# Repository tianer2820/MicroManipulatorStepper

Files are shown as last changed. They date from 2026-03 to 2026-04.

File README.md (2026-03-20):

# Open Micro-Manipulator

This project contains an open source low-cost, easy-to-build motorized **XYZ Micro-Manipulator** motion control platform achieving submicron precision.
It's designed for applications such as optical alignment, probing electronic components, and microscopy.

Check out the YouTube video for more information about the device and how it is built:<br>
[An Open Source Motorized XYZ Micro-Manipulator - Affordable sub µm Motion Control](https://youtu.be/MgQbPdiuUTw)

<div style="display: flex; gap: 2%;">
  
  
</div>

Thanks to its parallel kinematic structure and miniature ball joints, it achieves good mechanical stiffness and a large range of motion.
The motors are off the shelf stepper motors driven by a 30 kHz closed loop controller and a very precise PWM signal.
A 'magnetic gearing' approach increases the resolution of the low-cost magnetic rotary encoders by a factor of 30 allowing for steps down to 50nm
(**Please mind the difference between resolution and accuracy**. The absolute accuracy is significantly worse.

The device can be controlled via simple G-Code commands over a USB serial interface and is thus easily integrated into other projects.
The firmware implements a complete motion planning stack with look-ahead for smooth and accurate path following capabilities.

## Getting Started

Below is a list of high level steps you can follow if you want to replicate the project. 
If you have questions or problems with the build or just want to discuss subjects related to the project, 
joint the projects community [Discord Server](https://discord.gg/maRvMVpa2Q).

1. Read this Document and watch the linked videos
2. Get the parts listed in [Bill of Materials](documentation/bom/bom.md)
3. Build the device and electronics
4. Change the hardware configuration according to your build [hw_config.h](firmware/MotionControllerRP/src/hw_config.h)
5. Upload firmware using VSCode with PlattformIO plugin
6. Calibrate axis

Also check out the setup guide for new devices: [Setup Guide](documentation/setup_guide/setup_guide.md)

## ✨NEW: Hardware Version 4.0
A new version of the hardware has been released, fixing several issues with the previous design:

- Self collision during homing fixed.
- Connection of ball joint block with screws only was not well constrained and could rotated a bit.
- No reliable way to ensure consistent linkage rod length
- Unnecessary ball joint friction
- Accurate ball position heavily dependet on print quality and corner rounding
- Rubber bands could not be changed or removed once glued in.

A video about the improved ball joint and linkage manufactoring process can be found on YouTube: [Better Ball Joints for the Open Micro-Manipulator](https://www.youtube.com/watch?v=NM2KXvRGmpg)
Also the FreeCAD model was restructured and improved and now includes all pins and fasteners. It now provides a reference for all required mechanical parts. 

<div style="display: flex;">
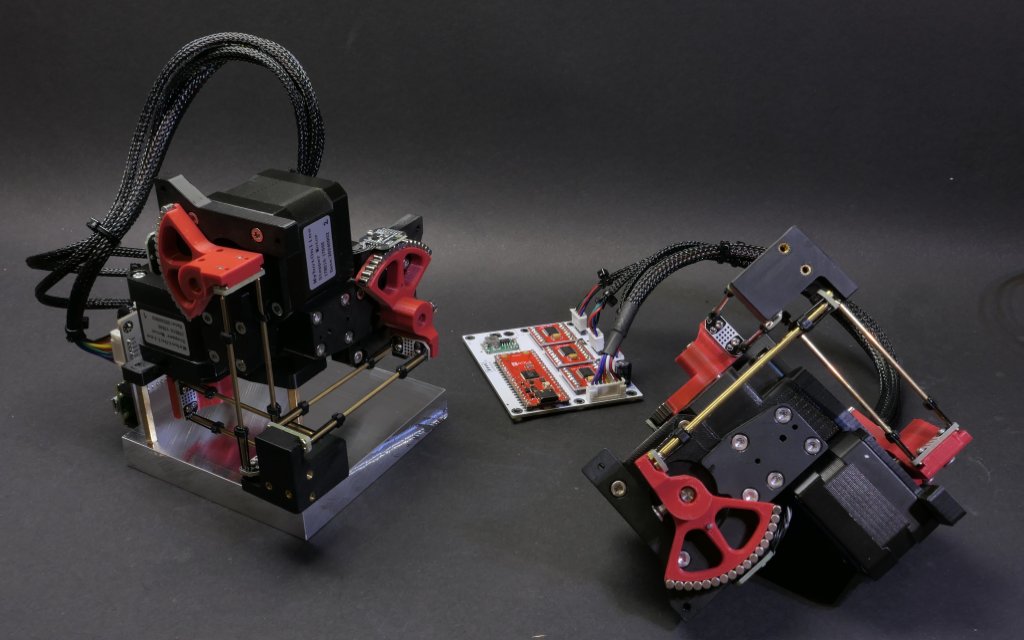
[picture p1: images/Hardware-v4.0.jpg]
Open Micro-Manipulator GUI
    
</div>

WARNING: BOM is not updated yet...

## Open Micro-Manipulator GUI
To make testing and using the Open-Micro Manipulator easy and convenient a python control program with a graphical user interface is provided here: [Open Micro-Manipulator GUI](https://github.com/0x23/OpenMicroManipulatorGUI).
It has simple controlls to move the device around, while also displaying a live camera feed (e.g. from a microscope camera). Additional features, include a simple g-code runner and realtime mouse control (e.g. for Biology applications).

<div style="display: flex;">
    Open Micro-Manipulator GUI
</div>

## 🐍 Python-API

The lightweight Python API handles all serial communication and provides convenient command execution and debug message printing.
The interface includes functions to home, move, and calibrate the device, as well as to query device information.

This library has not been published to pypi yet but it can be installed by running the following pip command. This can also be added to your projects requirements.txt:

```bash
pip3 install "git+https://github.com/0x23/MicroManipulatorStepper/#subdirectory=software/PythonAPI"
```

If you would like to use the calibration plotter then you will need the additional `plotter` optional dependency.

## Usage Example
```python
from open_micro_stage_api import OpenMicroStageInterface

# create interface and connect
oms = OpenMicroStageInterface(show_communication=True, show_log_messages=True)
oms.connect('/dev/ttyACM0')

# run this once to calibrate joints
# for i in range(3): oms.calibrate_joint(i, save_result=True)

# home device
oms.home()

# move to several x,y,z positions [mm]
oms.move_to(0.0, 0.0, 0.0, f=10)
oms.move_to(3.1, 4.1, 5.9, f=26)
oms.move_to(0.0001, 0.0, 0.0, f=10)

# wait for moves to finish
oms.wait_for_stop()
```

## API Functions (most relevant functions only)
```python
connect(port, baud_rate=921600)
disconnect()
set_workspace_transform(transform)
get_workspace_transform()
home(axis_list=None)
calibrate_joint(joint_index, save_result)
move_to(x, y, z, f, move_immediately, blocking, timeout)
set_tool_output(tool_idx, output_value, immediate)
set_pose(x, y, z)
dwell(time_s, blocking, timeout)
enable_motors(enable)
wait_for_stop(polling_interval_ms, disable_callbacks)
set_max_acceleration(linear_accel, angular_accel)
set_servo_parameter(pos_kp, pos_ki, vel_kp, vel_ki, vel_filter_tc)
```
## ✨ Firmware v1.0.4

Firmware 1.0.4 comes with many smaller improvements and bugfixes and a great new feature as well:

 - **Tools**: Tool usage (for example for laser engraving) is now supported on the two GPIO pins of J5 on the pcb.
              Tools are integrated into the planner and run fast and with correct timing when executing g-code.
              The tools support PWM (using the PIO feature to squeeze out extra channels without relying on software PWM).

   Example usage:
   ```
     M3 T0 S0.7  // set pwm output of tool 0 to 70%
     G4 S0.001   // dwell command (or any other motion command) - necessary to apply the tools output
   ```
   
- **Calibration**: Calibration has now some addition error checks to improve error reporting of potential problems like encoder alignment.
- **Kinematic Model Parameter**: Initialization code has been cleaned up and better comments where added to the parameters. Parameters are preset for HW v4.0 but you can toggle back to the old HW-v3.0 parameters if necessary.
- **Bugfixes**: smaller bugfixes

IMPORTANT: If you have **Hardware Version v3.0** you need to switch back to the old kinematic parameters in the [kinematic_model_delta3d.cpp](firmware/MotionControllerRP/src/kinematic_models/kinematic_model_delta3d.cpp) file (there is an #define for that at the top).

## Firmware v1.0.1

This update improves calibration, homing, logging, and adds several new G-Code commands.

### Improvements
- **Homing**: parallel homing support, higher repeatability, more accurate geometric reference  
- **Joint calibration**: refined procedure, persistent flash storage (no recalibration after reboot)  
- **Logging**: clearer and more detailed output  

### New G-Code Commands
- `G28` — Home joints (supports homing multiple axis simultanously for faster startup)
- `G24` — Set pose command (directly sets servo targets, bypassing motion controller)  
- `M17/M18` — Enable/Disable motors (with pose recovery from encoders on enable)  
- `M51` — Read encoder values  
- `M55` — Set servo loop parameters 
- `M56` — Joint calibration (with save-to-flash option)  
- `M57` — Read various information about the device state  
- `M58` — Read firmware version

## ⚙ CAD-Files

All CAD models are made in **FreeCAD** to allow everyone to view and modify the design without subscribing or paying for a proprietary CAD solution.
Note that most components are already designed with the goal to make them easily machinable on a 3-Axis CNC-Mill.
You can also 3D-Print the parts but have to live with thermal drift (carbon filled filaments can reduce this problem).

<div style="display: flex;">
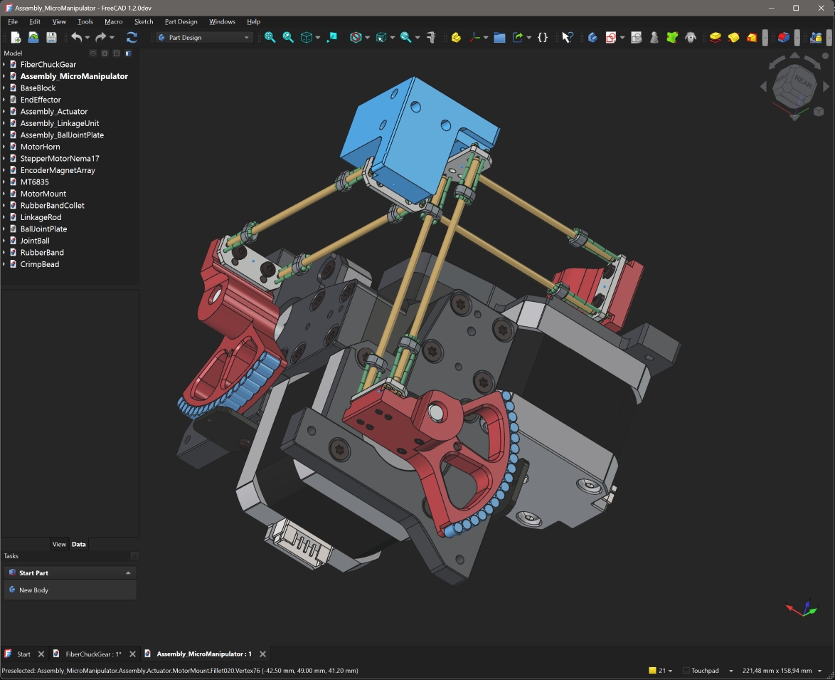
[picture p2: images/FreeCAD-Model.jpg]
FreeCAD Model
    
</div>

<br>

The CAD files can be found here: [CAD Models](construction).
Please note that FreeCAD version **1.2.0dev** was used, and the files might not work with older versions.

STL files for printing can be found here: [STL Files](construction/STL_3D_Printing/)

## ⚙ Kinematic Model

The kinematic model is defined here: [kinematic_model_delta3d.cpp](firmware/MotionControllerRP/src/kinemtaic_models/kinematic_model_delta3d.cpp).
Please check the dimensions of your build against the values set in the constructor. In particular, make sure the arm length matches.

## ⚙ Electronics

IMPORTANT: If you fabricated PCB version v1.2 (see version label on the board) you need to drill out a misplaced via on diode D1 that shorts 5V rail to ground (See [repair image](electronics/pcb_v1.2_fix.jpg) ). The problem was fixed in v1.3.

The electronics are designed in **KiCAD** and only commonly available modules (motor drivers and MCU boards) are used and connected by a simple PCB. No SMD soldering is required to populate the board to make the build extra accessible.
For usual winding resistance of your motors, the device should be powered by $${\color{lightgreen} 5V-6V }$$ (2A) to keep current and heating to a reasonable level.

<div style="display: flex; gap: 5%;">
  
  
</div>

The repository now also contains the fabrication files that can be directly uploaded to the PCB manufacturer.

## ⚙ Firmware

The firmware is written in C++ and takes some inspiration from the 'SimpleFOC' project. It aims to be streamlined and readable without any extra fuss, focusing on the hardware used in this project.
It implements path planning with look-ahead and, unlike many other motion controller projects, supports true 6DOF-Pose interpolation and planning, making it ready for driving hexapod motion platforms; that may or may not be the next step for this project.

You may find configuration for pin numbers, motor type, and other parameters in [hw_config.h](firmware/MotionControllerRP/src/hw_config.h). Please check them before uploading the firmware.

<div style="display: flex; gap: 2%;">
  
  
</div>

### Building and Flashing the Firmware

For building and flashing the firmware, Visual Studio Code (available for free on Windows and Linux) is recommended.
Install the PlatformIO add-on and open the firmware folder. You can now build and flash the firmware like any other PlatformIO project.

## ⚙ G-Code Interface

The firmware supports only a small subset of G-Code commands listed below.  
Each command is acknowledged with either an **`ok`** or **`error`** response.  

If a command provides additional information (e.g., the *get position* command), that information is returned **before** the `ok` message.  
The client must wait for an acknowledgment from the previous command before sending the next one—otherwise, behavior is undefined.
| Command           | Description                                                                 |
|-------------------|-----------------------------------------------------------------------------|
| `G0 X Y Z F`   | Move the end-effector in a straight line to the specified position. <br>• `X`, `Y`, `Z`: target positions <br>• `F`: feed rate |
| `G1 X Y Z F`   | Same as `G0`.                                                              |
| `G4 S/P`       | Dwell/pause for a specified time. <br>• `S`: seconds <br>• `P`: milliseconds |
| `G24 X Y Z A B C` | Directly set current pose for servo loops with optional rotation vector* `A`, `B`, `C`. |
| `G28 A-F`      | Home one or more joints. <br>• Optional joint selection `A`–`F`.           |
| `M3`           | Set Tool output. <br>• `T`: tool index <br>• `S`: output value (0.0..1.0) <br> Note: new values is only applied on the next motion or dwell command         |
| `M17`          | Enable motors and read current pose as the start pose.                     |
| `M18`          | Disable motors.                                                            |
| `M50`          | Get current internal pose. (Encoders are not read here)                                   |
| `M51`          | Get current encoder angles (in degrees) and raw encoder values.              |
| `M52`          | Get the number of items in the planner queue.                               |
| `M53`          | Check if all planned moves are finished (`1` = finished, `0` = not finished). |
| `M55 A B C D F` | Set servo loop parameters. <br>• `A`, `B`: position PI controller gains (P and I) <br>• `C`, `D`: velocity PI controller gains (P and I) <br>• `F`: velocity filter time constant |
| `M56 J S`      | Calibrate a joint. <br>• `J`: joint index <br>• `S`: save calibration result |
| `M57`          | Get device and servo loop info: homing/calibration state, angles, loop frequencies, and file list. |
| `M58`          | Get firmware version.                                                      |
| `M204 L A`     | Set linear and angular acceleration. <br>• `L`: linear acceleration <br>• `A`: angular acceleration |

*Note: The communication protocol uses 3D vectors for rotations. The direction represents the rotation axis and the length of the vector represents the angle of rotation around the axis.

## ❤️ Support

If you'd like to support this project, consider the following:

- **Contribute to the build guide** – Help improve or expand the build instructions by submitting pull requests or opening issues with suggestions.
- **Characterize typical radial stepper motor shaft error motion** – Measure radial error motion of the shaft of multiple Nema-17 stepper motors (see Cylos Garage for more information about the subject: https://www.youtube.com/watch?v=gt2gK-oxy5s).
- **Give feedback on the build experience** – Let us know what worked, what didn’t, and how the process could be smoother for others.
- **Support the project on Ko-fi** – If you find this project valuable, you can support it financially via [Ko-fi](https://ko-fi.com/diffractionlimited) ☕.

## Youtube Video
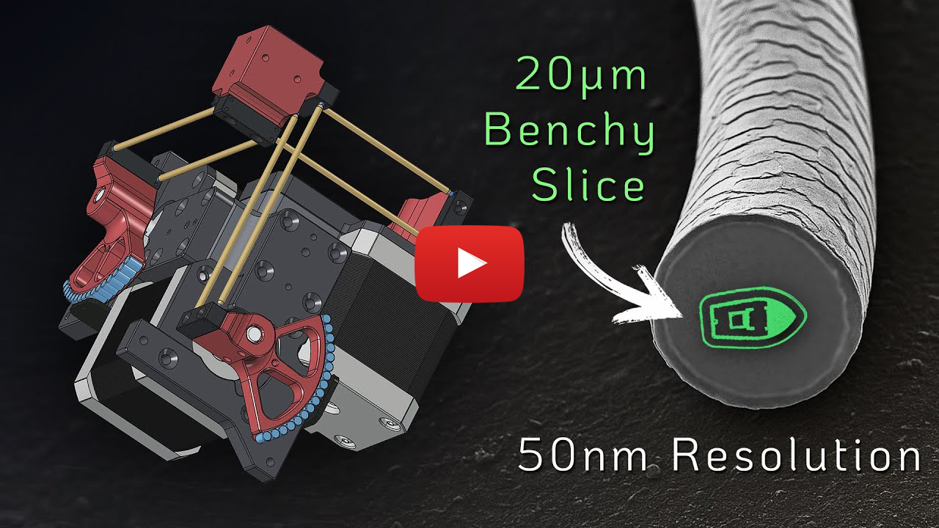
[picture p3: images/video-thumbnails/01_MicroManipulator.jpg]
Watch the video (https://youtu.be/MgQbPdiuUTw)

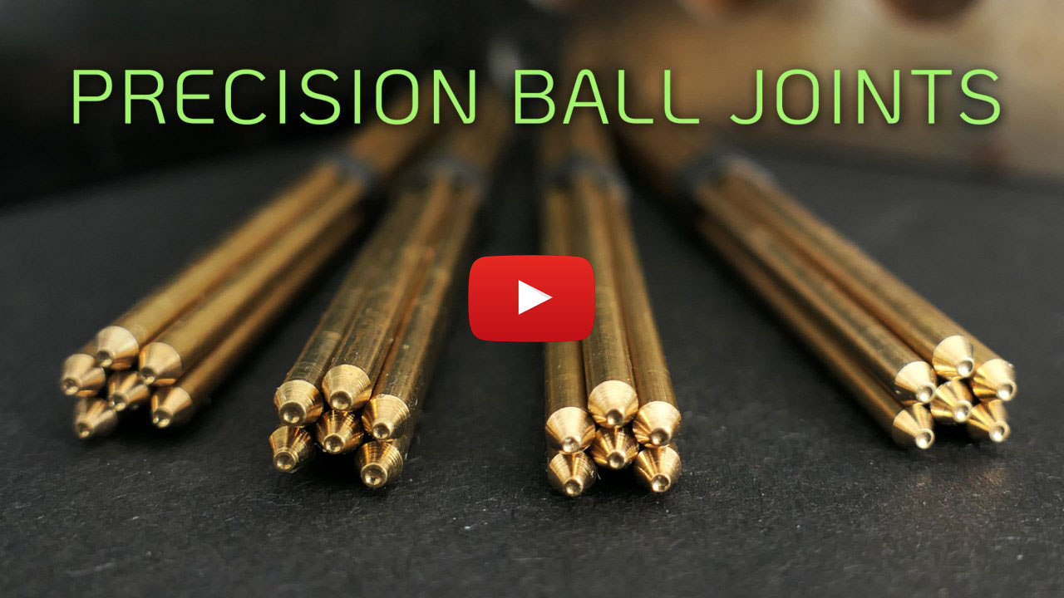
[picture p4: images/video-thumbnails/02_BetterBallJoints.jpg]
Better Ball Joints for the Open Micro-Manipulator (https://youtu.be/MgQbPdiuUTw)


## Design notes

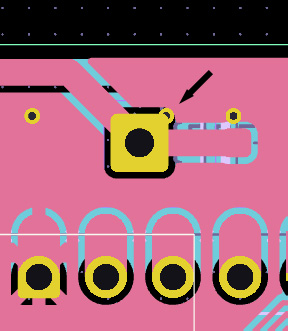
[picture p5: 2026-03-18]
electronics/control_board/pcb_v1.2_fix.jpg

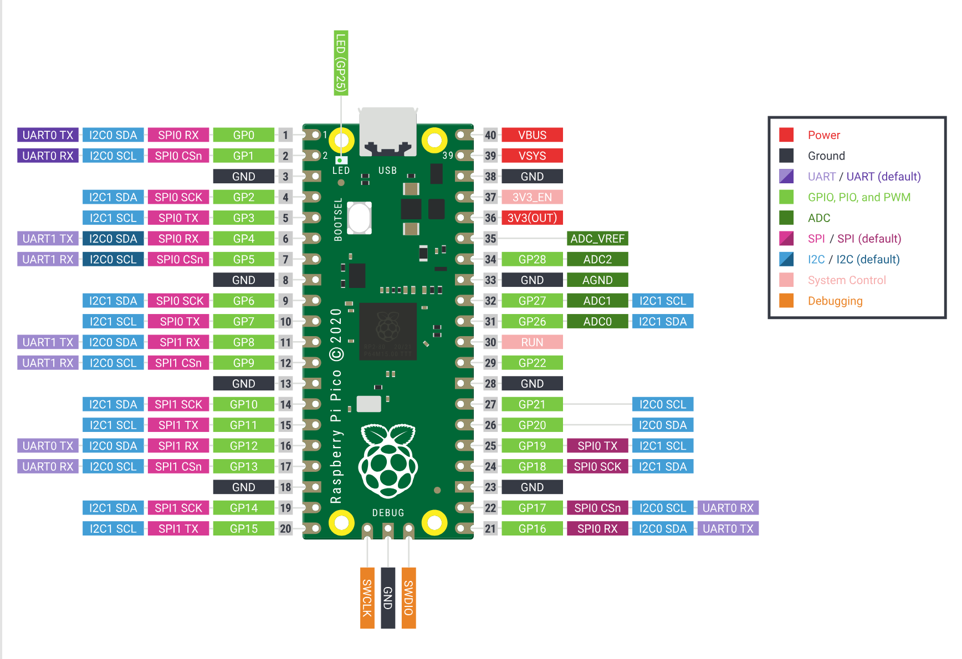
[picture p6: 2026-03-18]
firmware/MotionControllerRP/Rp2350-Pico_Pinout.png

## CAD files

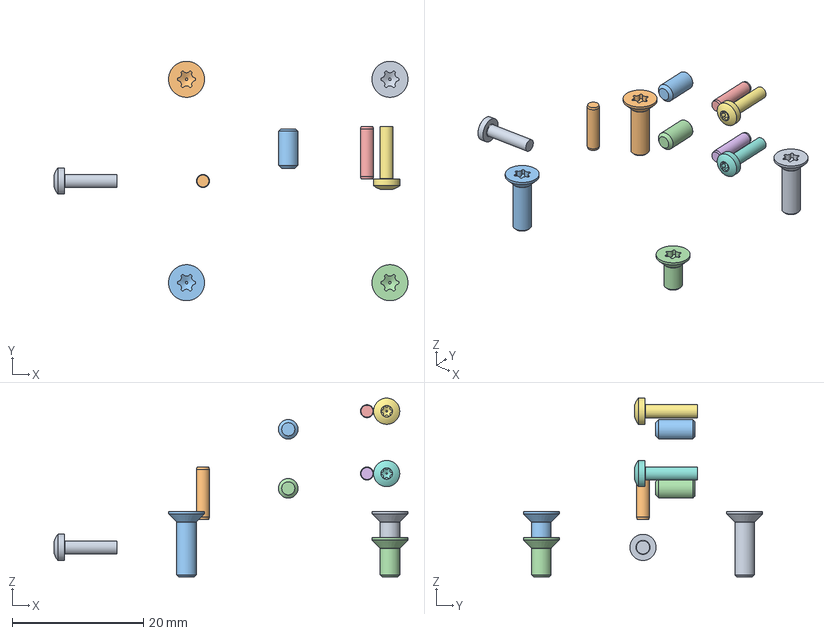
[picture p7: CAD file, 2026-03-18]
construction/micro_manipulator/Assembly_Actuator.FCStd
53.9 x 36.5 x 27.2 mm
M3x10-Screw x 2
M3x10-Screw008 x 2
M3x10-Screw009 x 2
M3x6-Screw x 2
2 mmx8-Pin x 2
2 mmx8-Pin012 x 2
M2x8-Screw x 2
M2x8-Screw009 x 2
M2x8-Screw004 x 2
2 mmx8-Pin011 x 2
M3x6-Screw003 x 2
M3x6-Screw004 x 2

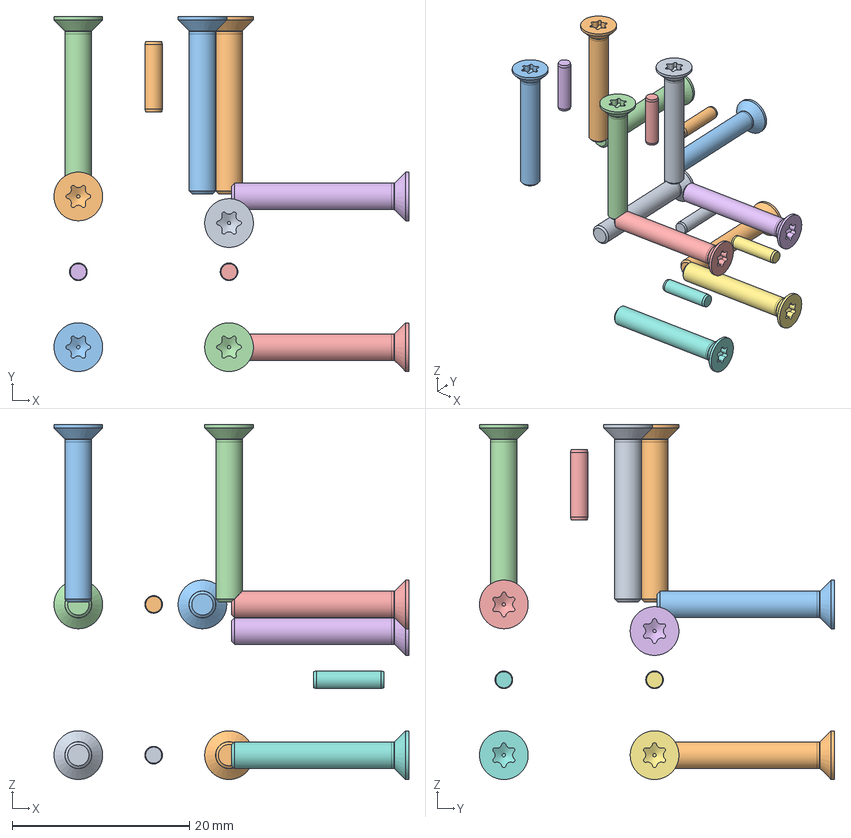
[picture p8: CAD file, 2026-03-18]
construction/micro_manipulator/Assembly_MicroManipulator.FCStd
40.0 x 40.0 x 40.0 mm
M3x20-Screw x 2
M3x20-Screw281 x 2
M3x20-Screw282 x 2
M3x20-Screw283 x 2
M3x20-Screw277 x 2
M3x20-Screw278 x 2
M3x20-Screw279 x 2
M3x20-Screw280 x 2
M3x20-Screw262 x 2
M3x20-Screw263 x 2
M3x20-Screw264 x 2
M3x20-Screw265 x 2
2 mmx8-Pin027 x 2
2 mmx8-Pin028 x 2
2 mmx8-Pin029 x 2
2 mmx8-Pin030 x 2
2 mmx8-Pin031 x 2
2 mmx8-Pin032 x 2

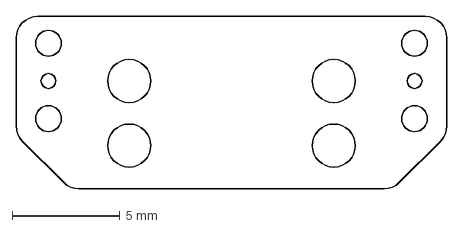
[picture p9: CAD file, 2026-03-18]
construction/micro_manipulator/balljoint_plate_pcb/BallJointPlate-Contour.dxf
20.0 x 8.00 mm

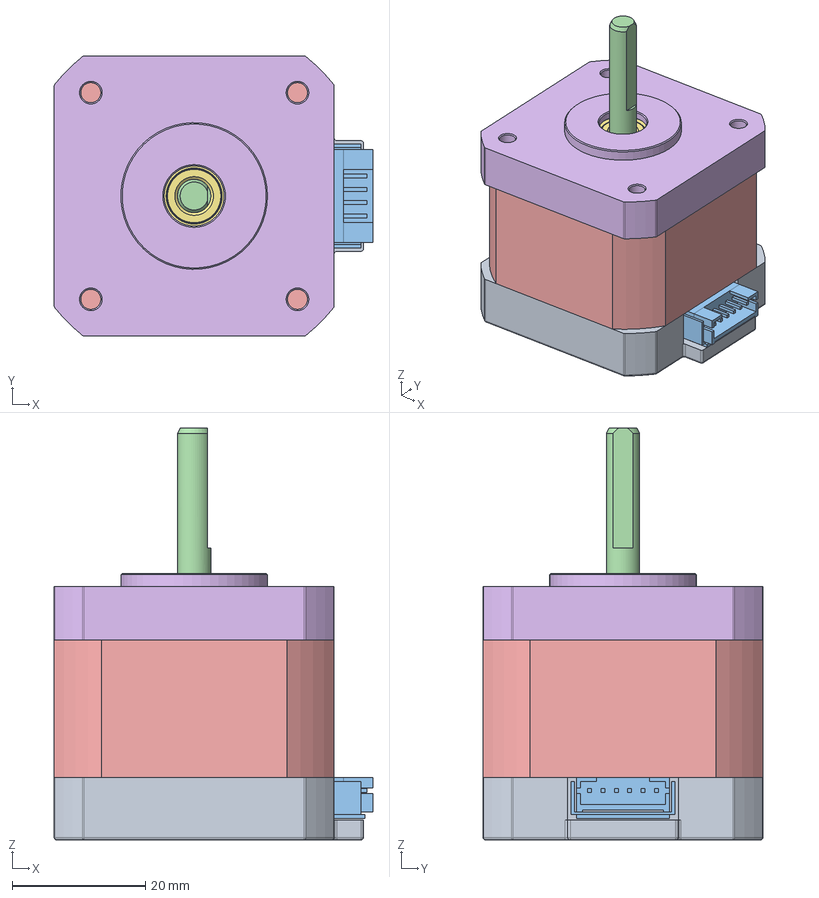
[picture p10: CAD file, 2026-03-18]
construction/micro_manipulator/StepperMotorNema17.FCStd
47.8 x 42.0 x 61.8 mm
rear end cap
rear bearing
connector
shaft
stator
front end cap
front bearing
M3x10-Screw
M3x10-Screw004
M3x10-Screw005
M3x10-Screw006

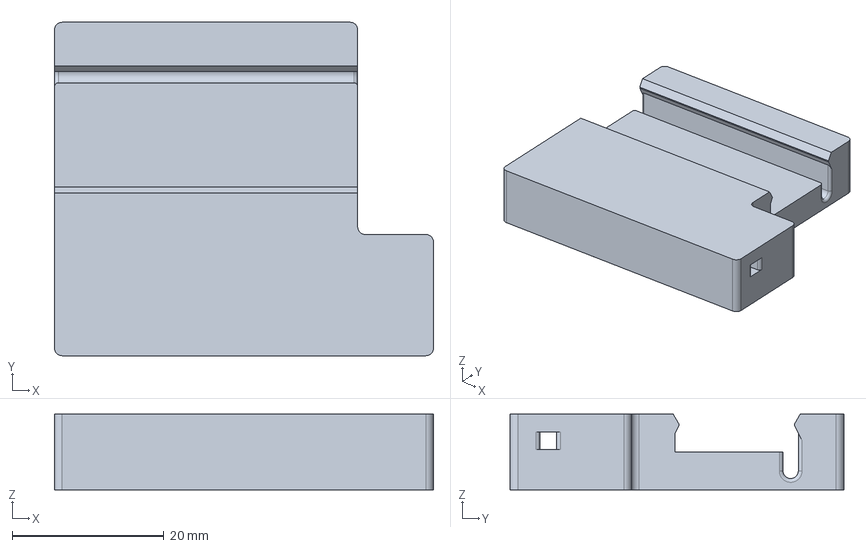
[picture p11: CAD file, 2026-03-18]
construction/tools/rod_embossing_tools/rod_lenth_setting_press/rod_guide.FCStd
50.0 x 44.0 x 10.0 mm

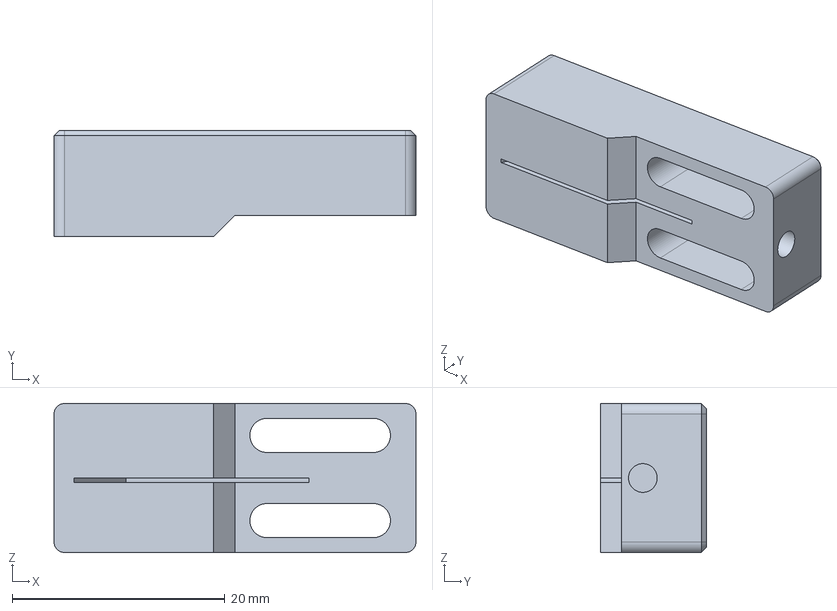
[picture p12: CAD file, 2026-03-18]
construction/tools/rod_embossing_tools/rod_sharper/BladeCarrier.FCStd
34.0 x 10.0 x 14.0 mm

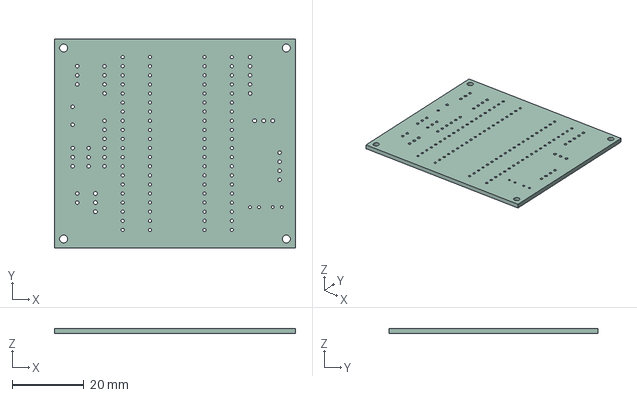
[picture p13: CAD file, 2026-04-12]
electronics/rot_platform_pcb/rot_platform_pcb.step
67.3 x 58.4 x 1.51 mm

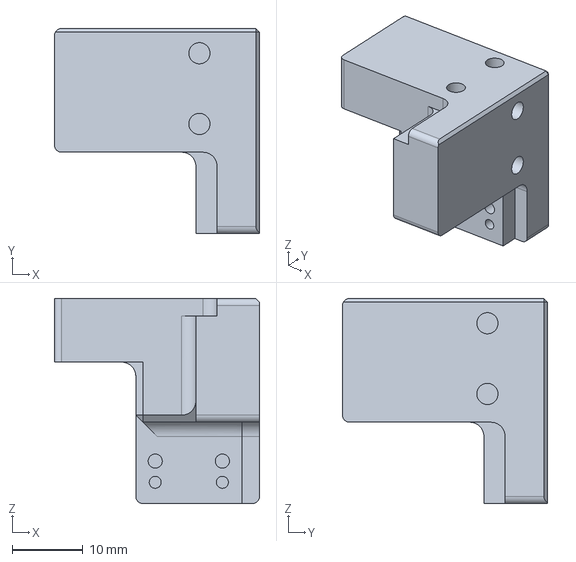
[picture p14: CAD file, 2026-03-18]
construction/micro_manipulator/EndEffector.FCStd
29.0 x 29.0 x 29.0 mm

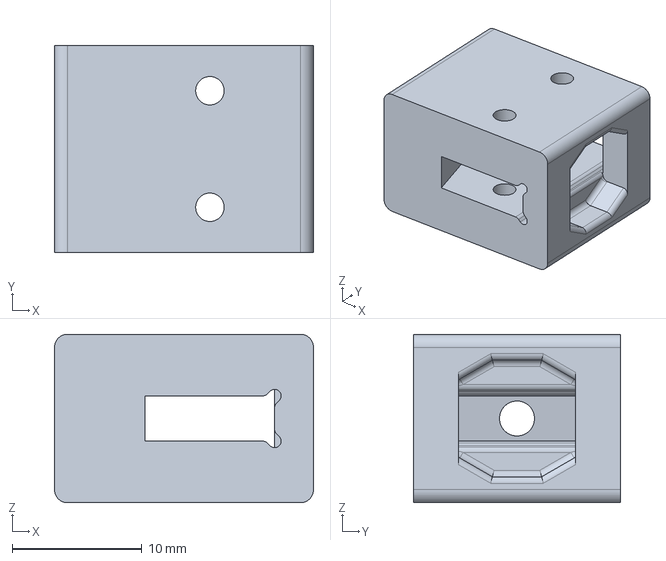
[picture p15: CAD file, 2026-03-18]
construction/tools/rod_embossing_tools/rod_lenth_setting_press/caliper_clamp.FCStd
20.0 x 16.0 x 13.0 mm

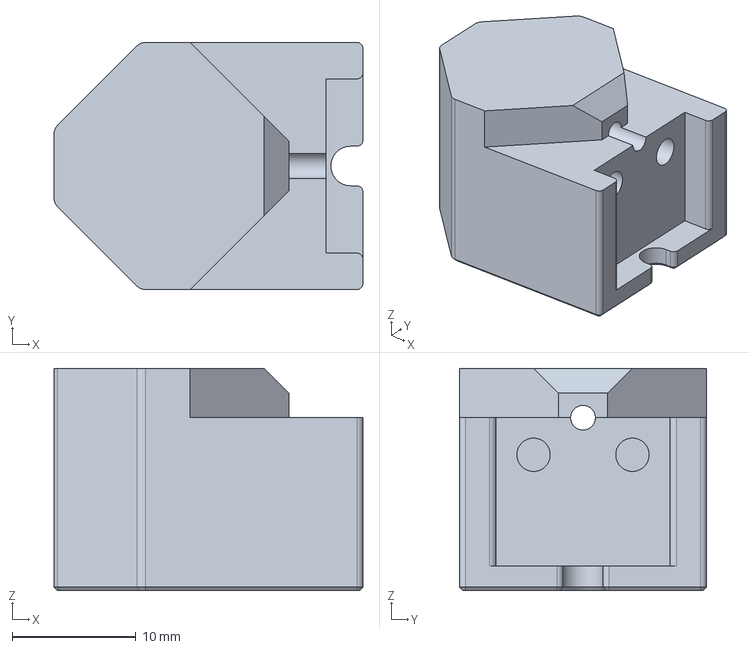
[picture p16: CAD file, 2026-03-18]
construction/tools/rod_embossing_tools/rod_sharper/RodGuide.FCStd
25.0 x 20.0 x 18.0 mm

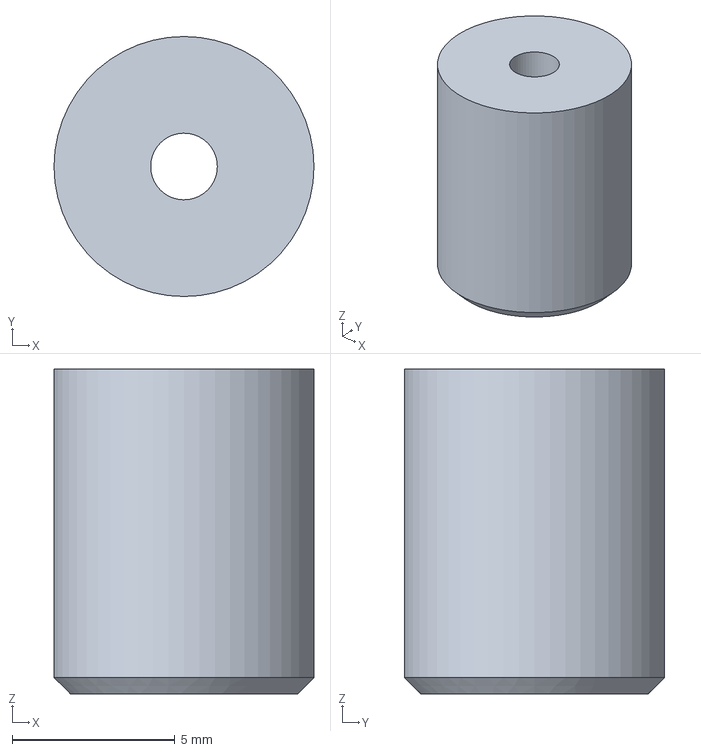
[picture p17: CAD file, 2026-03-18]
construction/tools/rod_embossing_tools/rod_lenth_setting_press/rod_collet.FCStd
8.00 x 8.00 x 10.0 mm

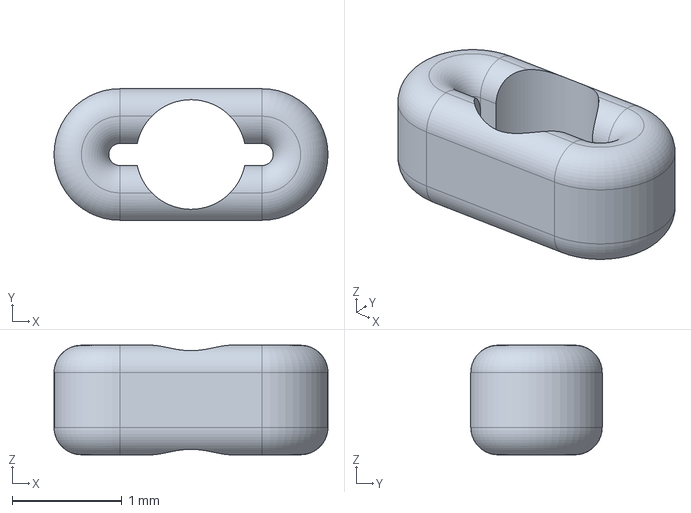
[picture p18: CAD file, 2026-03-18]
construction/micro_manipulator/CrimpBead.FCStd
2.50 x 1.20 x 1.00 mm

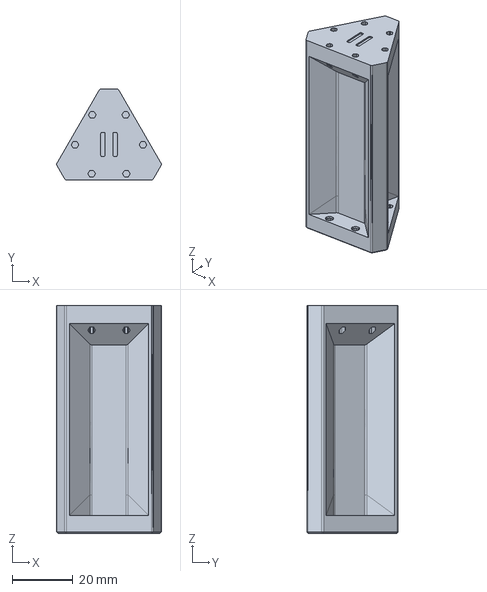
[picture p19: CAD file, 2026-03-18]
construction/tools/rod_embossing_tools/rod_lenth_setting_press/RodGrindingJig_B.FCStd
34.5 x 30.1 x 75.0 mm

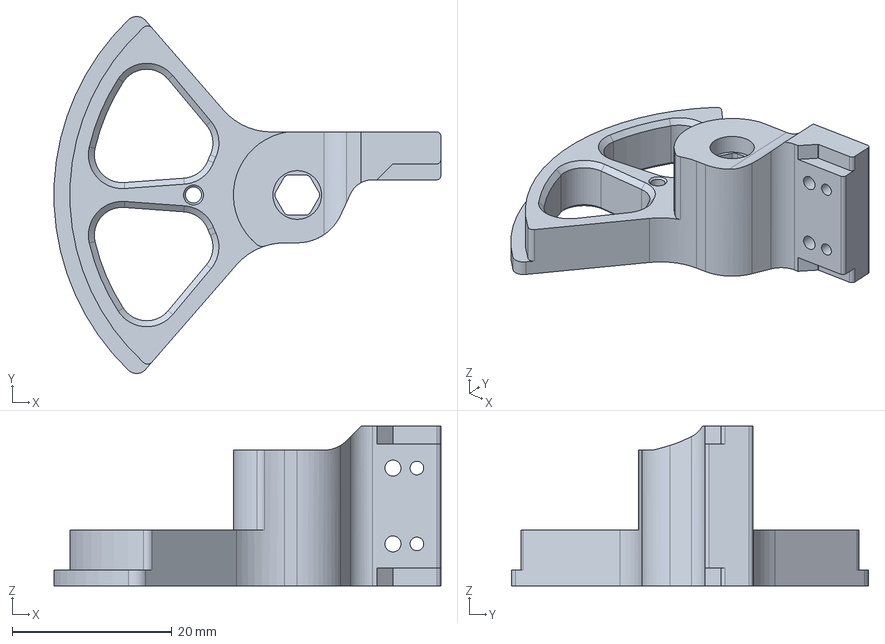
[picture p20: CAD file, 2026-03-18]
construction/micro_manipulator/MotorHorn.FCStd
48.5 x 44.7 x 20.0 mm

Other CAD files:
construction/micro_manipulator/Assembly_EndEffector.FCStd
construction/micro_manipulator/Assembly_BallJointPlate.FCStd
construction/micro_manipulator/Assembly_LinkageUnit.FCStd
construction/tools/rod_embossing_tools/rod_lenth_setting_press/RodGrindingJig_A.FCStd
construction/micro_manipulator/BallJointPlate.FCStd
construction/micro_manipulator/BaseBlock.FCStd
construction/micro_manipulator/EncoderMagnet.FCStd
construction/micro_manipulator/EncoderMagnetArray.FCStd
construction/micro_manipulator/JointBall.FCStd
construction/micro_manipulator/LinkageRod.FCStd
construction/micro_manipulator/MT6835.FCStd
construction/micro_manipulator/MotorMount.FCStd
construction/micro_manipulator/RubberBand.FCStd
construction/micro_manipulator/RubberBandCollet.FCStd

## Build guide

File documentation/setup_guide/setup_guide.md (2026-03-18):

# Setup Guide

This guide walks you through the setup of your new **Open Micro-Manipulator** device.

## Checklist for New Devices

1. **Was the mechanical limit pin added to the rotor?**  
   This pin is required for proper homing of the device.

    <div style="display: flex;">
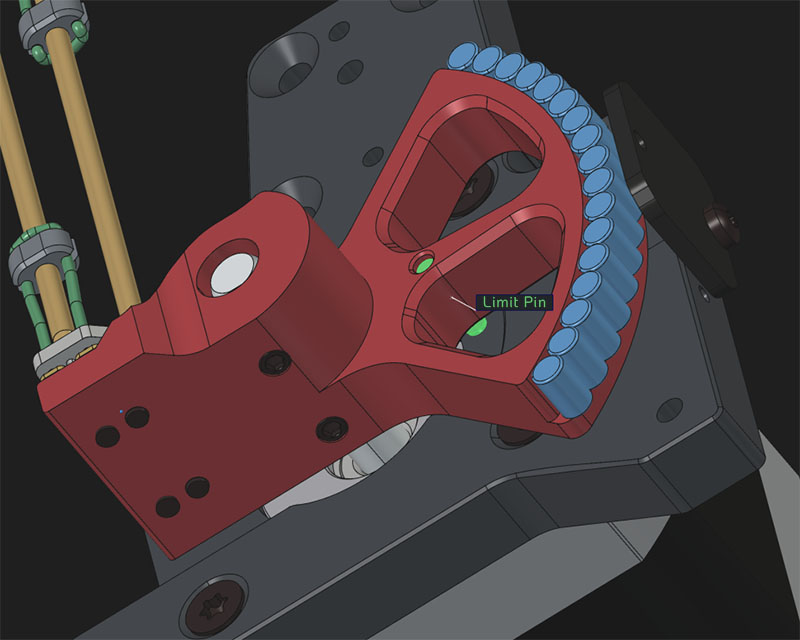
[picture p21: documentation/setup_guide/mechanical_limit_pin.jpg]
Mechanical Limit Pin
        
    </div>

2. **Are the screws that secure the rotor to the motor shaft installed?**  
   If the rotor is not firmly attached, it may slip imperceptibly during homing or other movements, leading to problems during calibration and homing.

3. **Is the homing direction correct?**  
   During the homing command (`G28`), the end effector should move toward the base.  
   If it moves in the opposite direction, rewire the motor to reverse its direction.

## Calibration and Checking the Encoders

You can use the calibration plotter to check if your encoders are working as expected.
On the left you see a good calibration on the right a bad calibration.

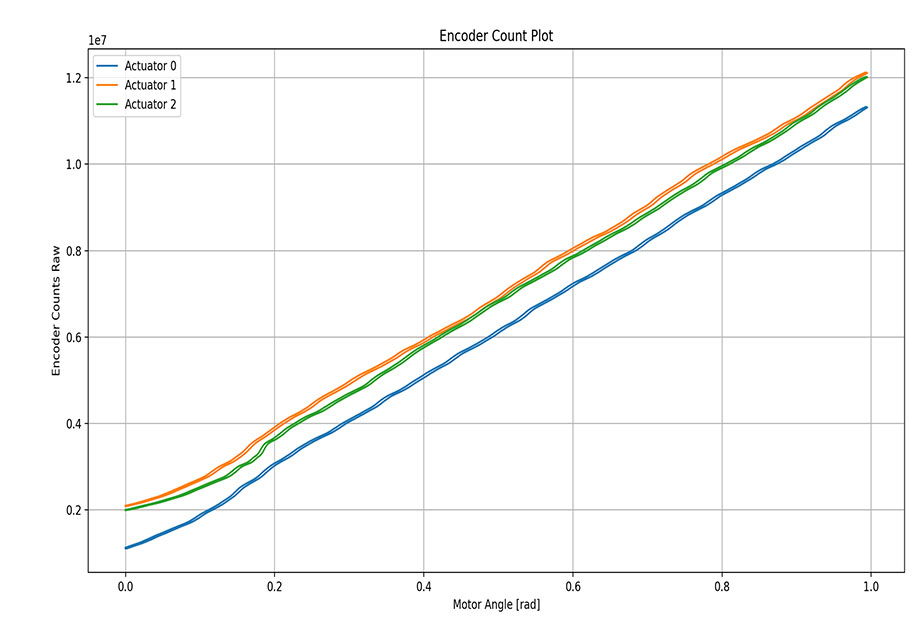
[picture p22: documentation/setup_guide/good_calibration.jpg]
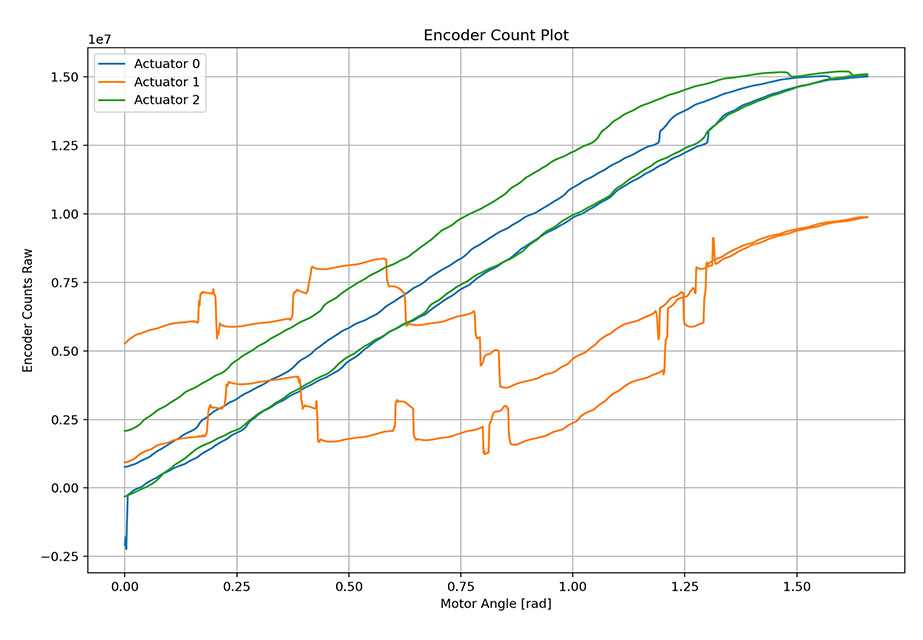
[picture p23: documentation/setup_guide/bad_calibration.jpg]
|  |  |
:--:|:--:
| **Good calibration** | **Bad calibration** |

THIS DOCUMENT IS UNFINISHED AND WORK IN PROGRESS...

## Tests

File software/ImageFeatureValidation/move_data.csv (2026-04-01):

From Position | To Position | Expected (um) | Actual (um) | Difference (um) | Feed
(-7.000000000,0.000000000) | (0.001000000,0.000000000) | 1 | 2.947063171 | 1.947063171 | 50
(0.001000000,0.000000000) | (0.002000000,0.000000000) | 1 | 1.324202497 | 0.324202497 | 50
(0.002000000,0.000000000) | (0.001000000,0.000000000) | 1 | 0.947177088 | -0.052822912 | 50
(0.001000000,0.000000000) | (0.000000000,0.000000000) | 1 | 1.716676845 | 0.716676845 | 50
(0.000000000,0.000000000) | (0.000000000,0.001000000) | 1 | 2.948005388 | 1.948005388 | 50
(0.000000000,0.001000000) | (0.000000000,0.002000000) | 1 | 2.185358535 | 1.185358535 | 50
(0.000000000,0.002000000) | (0.000000000,0.001000000) | 1 | 1.970507707 | 0.970507707 | 50
(0.000000000,0.001000000) | (0.000000000,0.000000000) | 1 | 2.121842258 | 1.121842258 | 50
(0.000000000,0.000000000) | (0.000707000,0.000707000) | 0.999848989 | 2.444252178 | 1.444403189 | 50
(0.000707000,0.000707000) | (0.001414000,0.001414000) | 0.999848989 | 2.787920685 | 1.788071696 | 50
(0.001414000,0.001414000) | (0.000707000,0.000707000) | 0.999848989 | 2.839523164 | 1.839674176 | 50
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

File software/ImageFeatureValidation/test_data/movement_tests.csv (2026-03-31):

x | y | feed | delay
0.001000 | 0.000000 | 50.0
0.002000 | 0.000000 | 50.0
0.001000 | 0.000000 | 50.0
0.000000 | 0.000000 | 50.0
0.000000 | 0.001000 | 50.0
0.000000 | 0.002000 | 50.0
0.000000 | 0.001000 | 50.0
0.000000 | 0.000000 | 50.0
0.000707 | 0.000707 | 50.0
0.001414 | 0.001414 | 50.0
0.000707 | 0.000707 | 50.0
0.000000 | 0.000000 | 50.0
-0.000707 | 0.000707 | 50.0
0.000000 | 0.001414 | 50.0
0.000707 | 0.000707 | 50.0
0.000000 | 0.000000 | 50.0
0.001000 | 0.000000 | 50.0
0.000293 | 0.000707 | 50.0
0.001000 | 0.001414 | 50.0
0.001707 | 0.000707 | 50.0
0.001000 | 0.000000 | 50.0
0.000000 | 0.000000 | 50.0
-0.000707 | -0.000707 | 50.0
0.000293 | -0.000707 | 50.0
0.001293 | -0.000707 | 50.0
0.000586 | 0.000000 | 50.0
0.000000 | 0.000000 | 50.0
0.001000 | 0.000000 | 50.0
0.002000 | 0.000000 | 50.0
0.001000 | 0.000000 | 50.0
0.000000 | 0.000000 | 50.0
0.000000 | 0.001000 | 50.0
0.000000 | 0.002000 | 50.0
0.000000 | 0.001000 | 50.0
0.000000 | 0.000000 | 50.0
0.000707 | 0.000707 | 50.0
0.001414 | 0.001414 | 50.0
0.000707 | 0.000707 | 50.0
0.000000 | 0.000000 | 50.0
-0.000707 | 0.000707 | 50.0
0.000000 | 0.001414 | 50.0
0.000707 | 0.000707 | 50.0
0.000000 | 0.000000 | 50.0
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

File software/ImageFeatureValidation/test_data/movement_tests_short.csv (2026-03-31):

x | y | feed | delay
0.01000 | 0.00000 | 50.0
0.02000 | 0.00000 | 50.0
0.01000 | 0.00000 | 50.0
0.00000 | 0.00000 | 50.0
0.00000 | 0.01000 | 50.0
0.00000 | 0.02000 | 50.0
0.00000 | 0.01000 | 50.0
0.00000 | 0.00000 | 50.0
0.00707 | 0.00707 | 50.0
0.01414 | 0.01414 | 50.0
0.00707 | 0.00707 | 50.0
0.00000 | 0.00000 | 50.0
-0.00707 | 0.00707 | 50.0
0.00000 | 0.01414 | 50.0
0.00707 | 0.00707 | 50.0
0.00000 | 0.00000 | 50.0
0.01000 | 0.00000 | 50.0
0.00293 | 0.00707 | 50.0
0.01000 | 0.01414 | 50.0
0.01707 | 0.00707 | 50.0
0.01000 | 0.00000 | 50.0
0.00000 | 0.00000 | 50.0
-0.00707 | -0.00707 | 50.0
0.00293 | -0.00707 | 50.0
0.01293 | -0.00707 | 50.0
0.00586 | 0.00000 | 50.0
0.00000 | 0.00000 | 50.0

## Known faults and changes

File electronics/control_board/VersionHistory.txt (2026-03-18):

*** v1.3 ****************************

 - Fixed critical problem with PCB layout, where 5V rail was shorted to GND on one of the diode pins of D1.
 
*** v1.2 ****************************

- added diode on 5V mcu supply to prevent motors from being powered backwards through the stepdown converter.

*** v1.1 ****************************

- Silkscreen on encoder connector was wrong: labels for CS1 and CS3 where swapped

*** v1.0 ****************************

Initial version

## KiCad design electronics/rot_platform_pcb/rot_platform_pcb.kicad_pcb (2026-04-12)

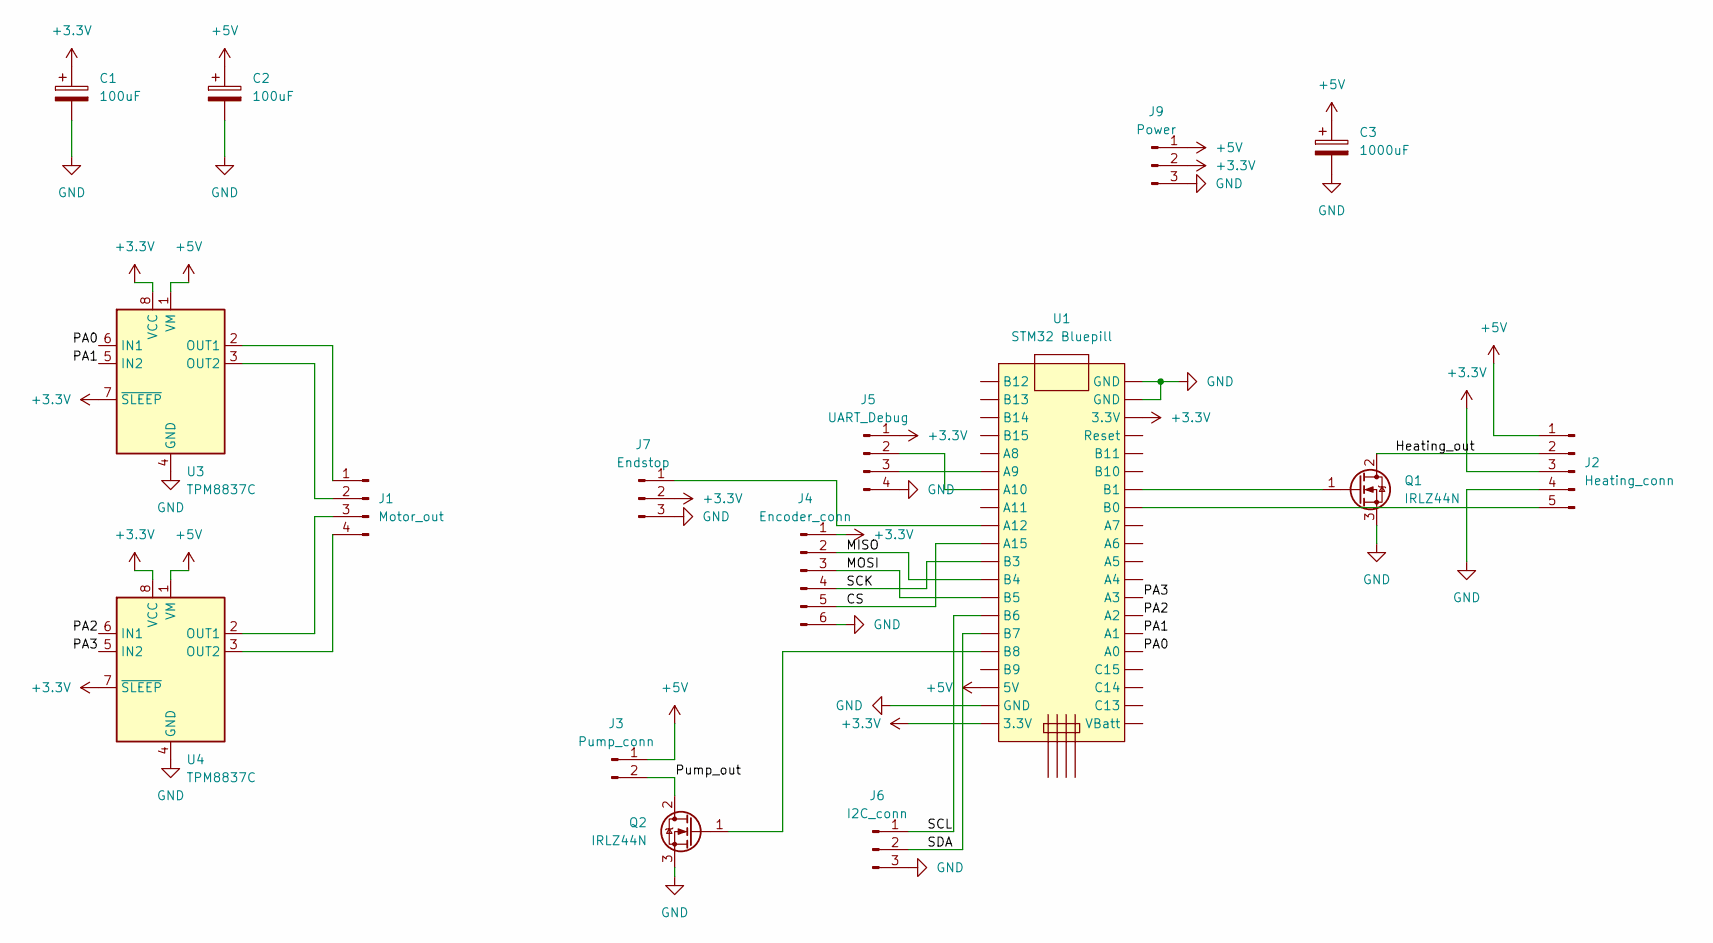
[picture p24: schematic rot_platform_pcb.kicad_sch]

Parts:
C1, C2: 100uF; CP_Radial_D5.0mm_P2.50mm
C3: 1000uF; CP_Radial_D10.0mm_P5.00mm
J1: Motor_out; PinHeader_1x04_P2.54mm_Vertical
J2: Heating_conn; PinHeader_1x05_P2.54mm_Vertical
J3: Pump_conn; PinHeader_1x02_P2.54mm_Vertical
J4: Encoder_conn; PinHeader_1x06_P2.54mm_Vertical
J5: UART_Debug; PinHeader_1x04_P2.54mm_Vertical
J6: I2C_conn; PinHeader_1x03_P2.54mm_Vertical
J7: Endstop; PinHeader_1x03_P2.54mm_Vertical
J9: Power; PinHeader_1x03_P2.54mm_Vertical
Q1, Q2: IRLZ44N; TO-220-3_Vertical
U1: STM32 Bluepill; stm32_bluepill
U3, U4: TPM8837C; SOIC-8-1EP_3.9x4.9mm_P1.27mm_EP2.29x3mm

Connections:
+3.3V: C1.1, J2.3, J4.1, J5.1, J7.2, J9.2, U1.20 (3.3V), U1.38 (3.3V), U3.7 (~SLEEP), U3.8 (VCC), U4.7 (~SLEEP), U4.8 (VCC)
+5V: C2.1, C3.1, J2.1, J3.1, J9.1, U1.18 (5V), U3.1 (VM), U4.1 (VM)
/CS: J4.5, U1.10 (A15)
/Heating_out: J2.2, Q1.2 (D)
/MISO: J4.2, U1.12 (B4)
/MOSI: J4.3, U1.13 (B5)
/PA0: U1.25 (A0), U3.6 (IN1)
/PA1: U1.26 (A1), U3.5 (IN2)
/PA2: U1.27 (A2), U4.6 (IN1)
/PA3: U1.28 (A3), U4.5 (IN2)
/Pump_out: J3.2, Q2.2 (D)
/SCK: J4.4, U1.11 (B3)
/SCL: J6.1, U1.14 (B6)
/SDA: J6.2, U1.15 (B7)
GND: C1.2, C2.2, C3.2, J2.4, J4.6, J5.4, J6.3, J7.3, J9.3, Q1.3 (S), Q2.3 (S), U1.19 (GND), U1.39 (GND), U1.40 (GND), U3.4 (GND), U3.9 (GND), U4.4 (GND), U4.9 (GND)
unnamed: J1.1, U3.2 (OUT1)
unnamed: J1.2, U3.3 (OUT2)
unnamed: J1.3, U4.2 (OUT1)
unnamed: J1.4, U4.3 (OUT2)
unnamed: J2.5, U1.33 (B0)
unnamed: J5.2, U1.7 (A10)
unnamed: J5.3, U1.6 (A9)
unnamed: J7.1, U1.9 (A12)
unnamed: Q1.1 (G), U1.34 (B1)
unnamed: Q2.1 (G), U1.16 (B8)

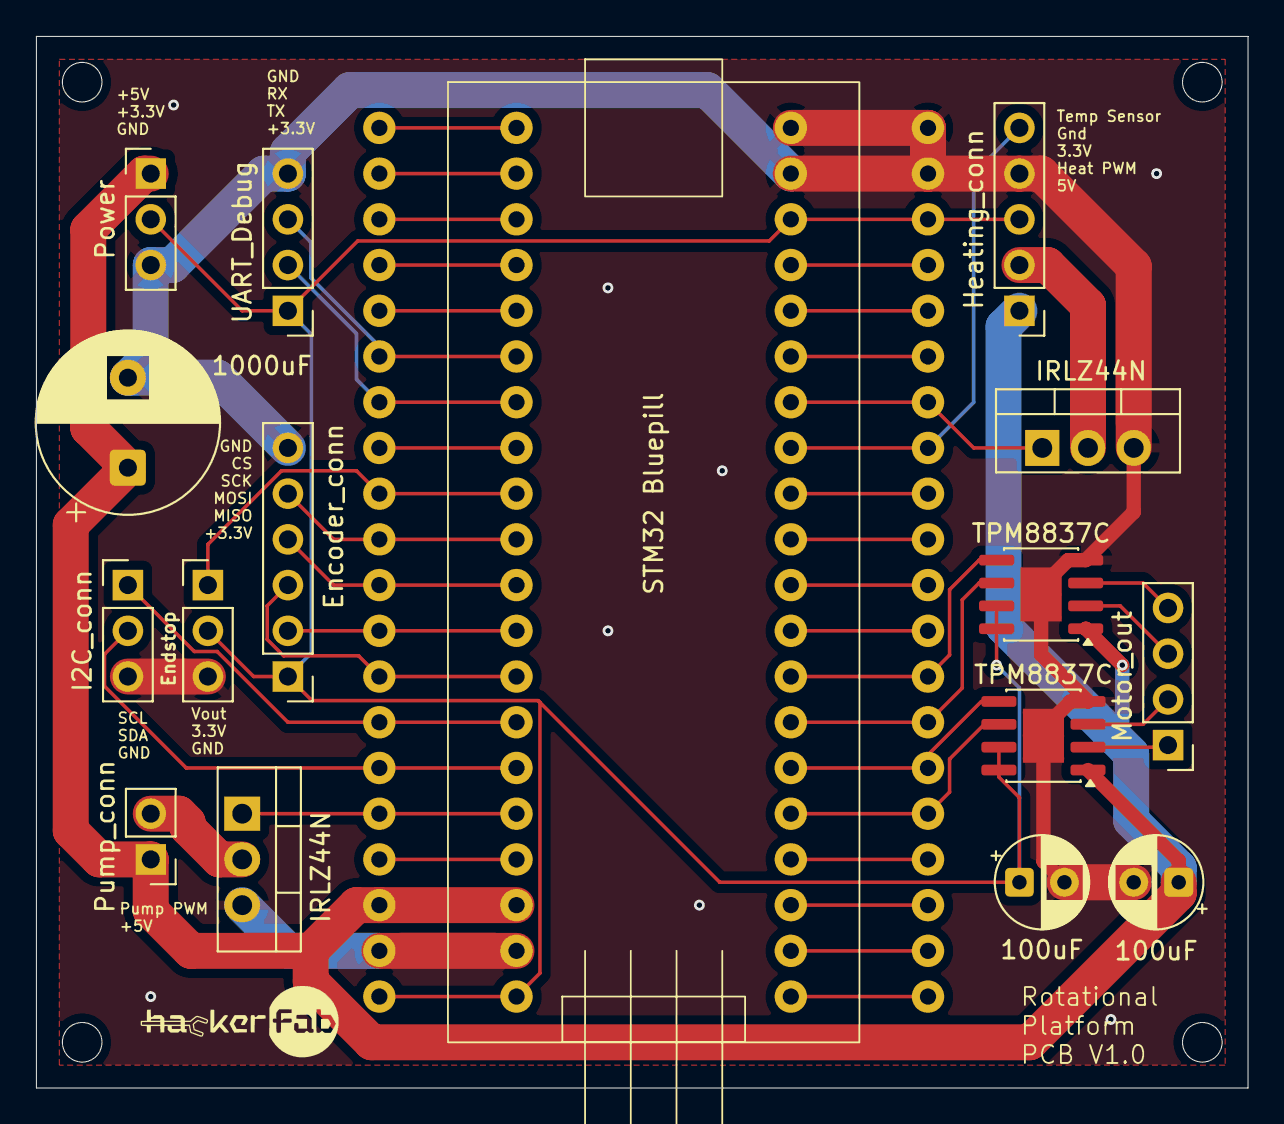
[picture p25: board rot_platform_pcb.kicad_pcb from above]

Board: 2 copper layers, 67.3 x 58.4 mm, 16 parts (0 on the bottom side), 25 nets.

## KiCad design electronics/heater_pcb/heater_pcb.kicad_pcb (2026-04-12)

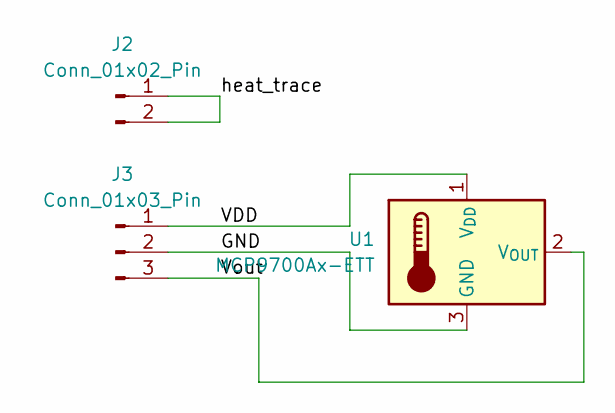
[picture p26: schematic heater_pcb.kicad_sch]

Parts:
J2: Conn_01x02_Pin; PinHeader_1x02_P2.54mm_Vertical
J3: Conn_01x03_Pin; PinHeader_1x03_P2.54mm_Vertical
U1: MCP9700Ax-ETT; SOT-23

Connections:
/GND: J3.2, U1.3 (GND)
/VDD: J3.1, U1.1 (V_{DD})
/Vout: J3.3, U1.2 (V_{OUT})
/heat_trace: J2.1, J2.2

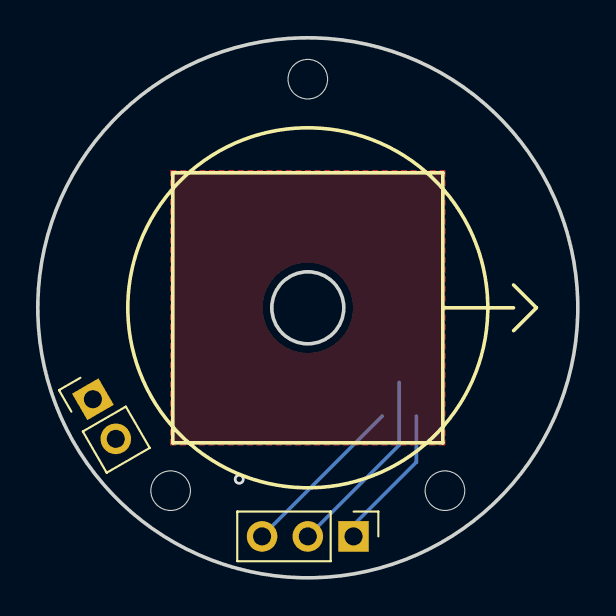
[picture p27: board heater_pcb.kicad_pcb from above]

Board: 4 copper layers, 30.0 x 30.0 mm, 3 parts (1 on the bottom side), 4 nets.

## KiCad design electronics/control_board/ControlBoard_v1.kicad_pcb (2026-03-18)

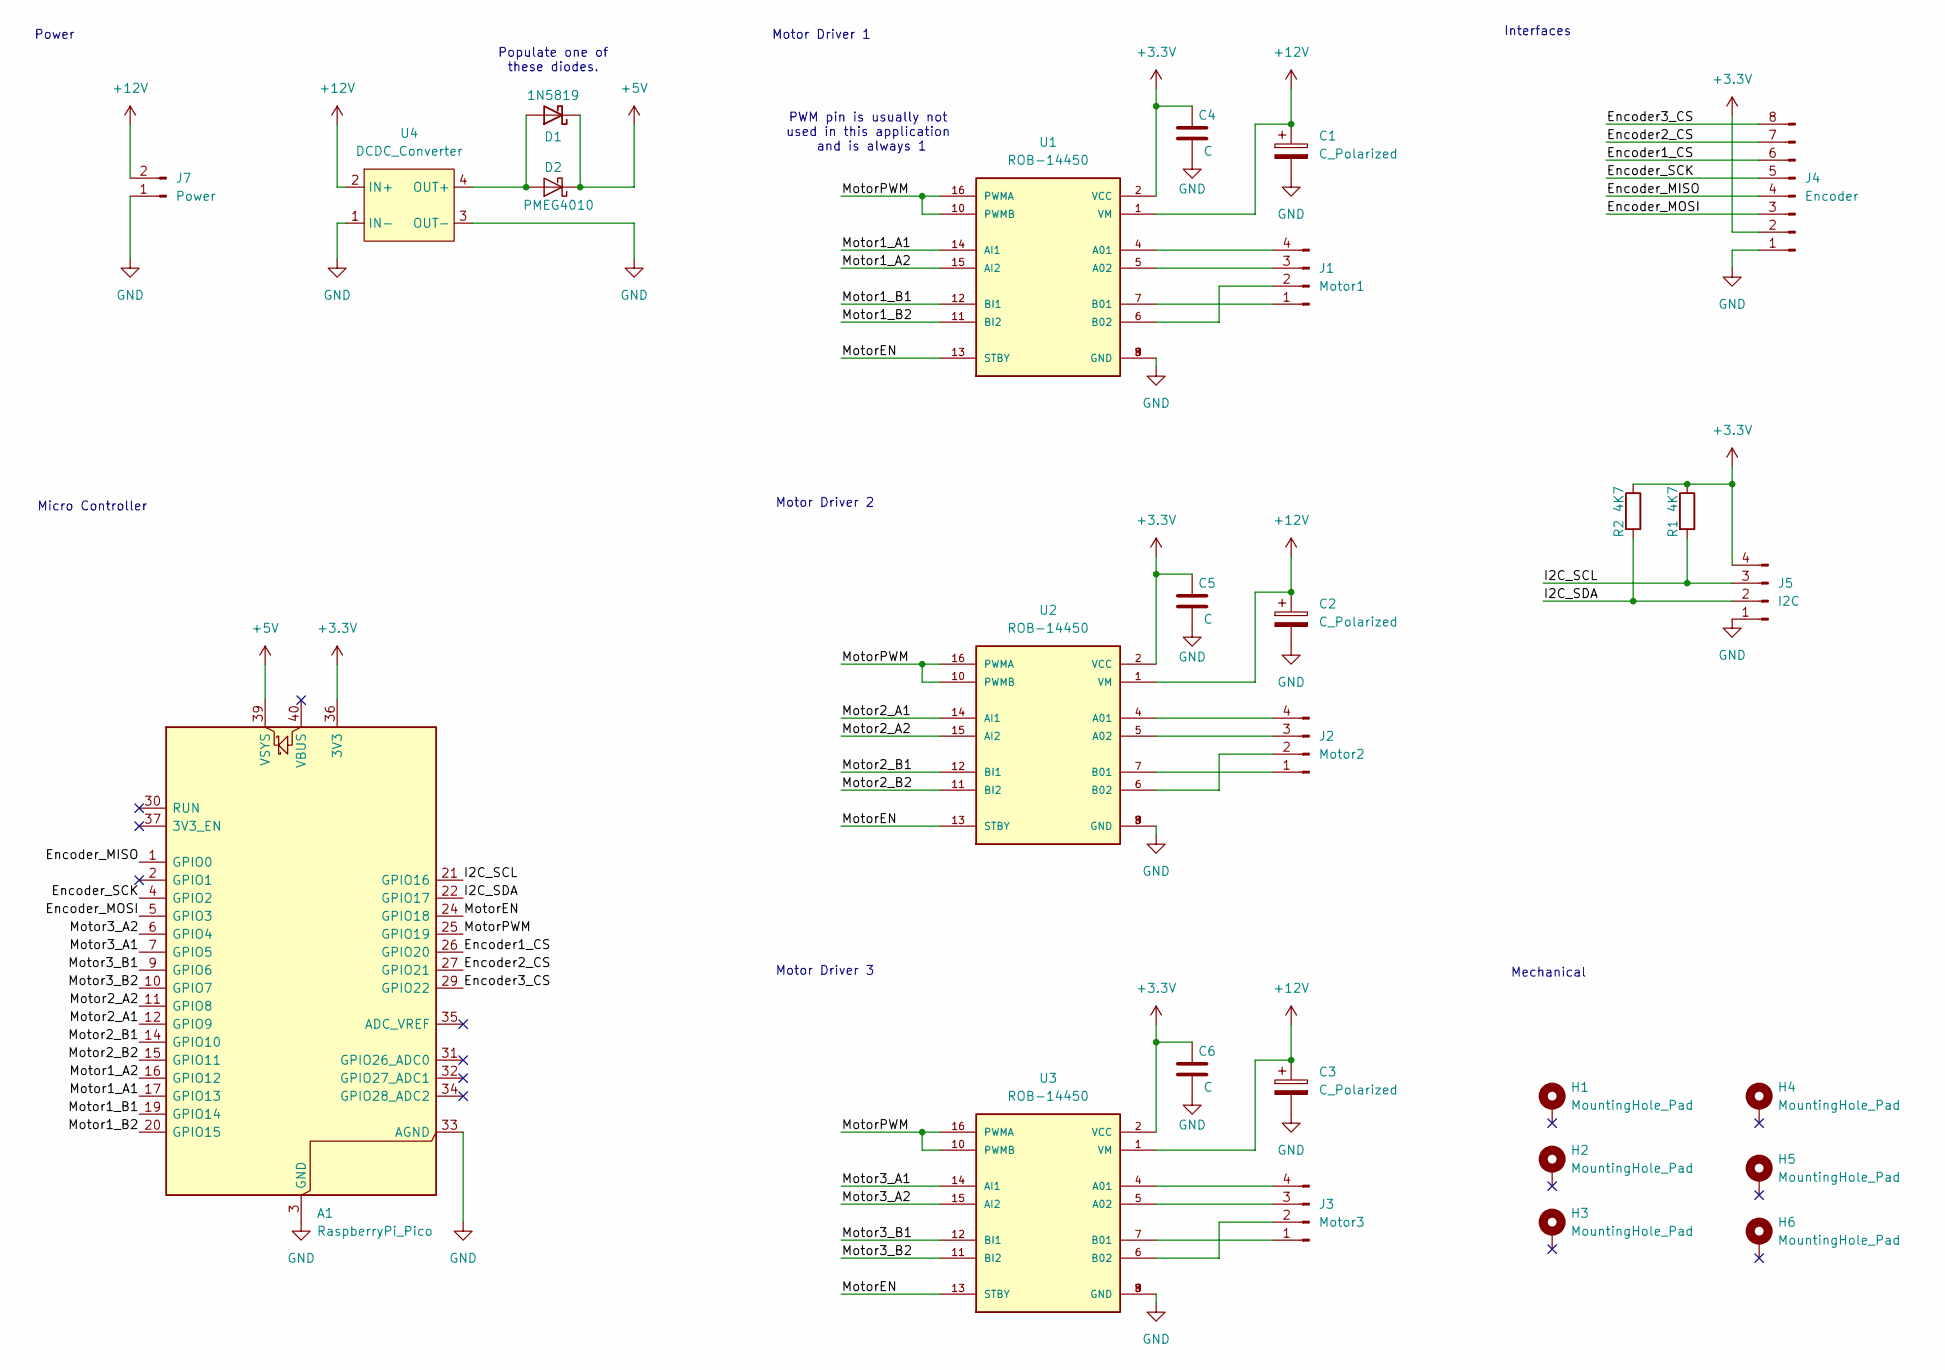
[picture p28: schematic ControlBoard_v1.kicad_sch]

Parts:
A1: RaspberryPi_Pico; RaspberryPi_Pico_Common_Unspecified
C1, C2, C3: C_Polarized; CP_Radial_D8.0mm_P3.50mm
C4, C5, C6: C; C_0603_1608Metric_Pad1.08x0.95mm_HandSolder
D1: 1N5819; D_DO-41_SOD81_P10.16mm_Horizontal
D2: PMEG4010; D_SOD-123F
H1, H2, H3, H4, H5, H6: MountingHole_Pad; MountingHole_2.7mm_M2.5_Pad_Via
J1: Motor1; PinHeader_1x04_P2.54mm_Vertical
J2: Motor2; PinHeader_1x04_P2.54mm_Vertical
J3: Motor3; PinHeader_1x04_P2.54mm_Vertical
J4: Encoder; JST_PH_B8B-PH-K_1x08_P2.00mm_Vertical
J5: I2C; JST_PH_B4B-PH-K_1x04_P2.00mm_Vertical
J7: Power; AMASS_XT60-M_1x02_P7.20mm_Vertical
R1, R2: 4K7; R_0603_1608Metric_Pad0.98x0.95mm_HandSolder
U1, U2, U3: ROB-14450; MODULE_ROB-14450; PARTREV 11-13-17
U4: DCDC_Converter; DCDC_17mmx12mm

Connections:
+3.3V: A1.36 (3V3), C4.1, C5.1, C6.1, J4.2, J5.4, R1.1, R2.1, U1.2 (VCC), U2.2 (VCC), U3.2 (VCC)
+5V: A1.39 (VSYS), D1.1 (K), D2.1 (K)
+12V: C1.1, C2.1, C3.1, J7.2, U1.1 (VM), U2.1 (VM), U3.1 (VM), U4.2 (IN+)
/Encoder1_CS: A1.26 (GPIO20), J4.6
/Encoder2_CS: A1.27 (GPIO21), J4.7
/Encoder3_CS: A1.29 (GPIO22), J4.8
/Encoder_MISO: A1.1 (GPIO0), J4.4
/Encoder_MOSI: A1.5 (GPIO3), J4.3
/Encoder_SCK: A1.4 (GPIO2), J4.5
/I2C_SCL: A1.21 (GPIO16), J5.3, R1.2
/I2C_SDA: A1.22 (GPIO17), J5.2, R2.2
/Motor1_A1: A1.17 (GPIO13), U1.14 (AI1)
/Motor1_A2: A1.16 (GPIO12), U1.15 (AI2)
/Motor1_B1: A1.19 (GPIO14), U1.12 (BI1)
/Motor1_B2: A1.20 (GPIO15), U1.11 (BI2)
/Motor2_A1: A1.12 (GPIO9), U2.14 (AI1)
/Motor2_A2: A1.11 (GPIO8), U2.15 (AI2)
/Motor2_B1: A1.14 (GPIO10), U2.12 (BI1)
/Motor2_B2: A1.15 (GPIO11), U2.11 (BI2)
/Motor3_A1: A1.7 (GPIO5), U3.14 (AI1)
/Motor3_A2: A1.6 (GPIO4), U3.15 (AI2)
/Motor3_B1: A1.9 (GPIO6), U3.12 (BI1)
/Motor3_B2: A1.10 (GPIO7), U3.11 (BI2)
/MotorEN: A1.24 (GPIO18), U1.13 (STBY), U2.13 (STBY), U3.13 (STBY)
/MotorPWM: A1.25 (GPIO19), U1.10 (PWMB), U1.16 (PWMA), U2.10 (PWMB), U2.16 (PWMA), U3.10 (PWMB), U3.16 (PWMA)
GND: A1.3 (GND), A1.8 (GND), A1.13 (GND), A1.18 (GND), A1.23 (GND), A1.28 (GND), A1.33 (AGND), A1.38 (GND), C1.2, C2.2, C3.2, C4.2, C5.2, C6.2, J4.1, J5.1, J7.1, U1.3 (GND), U1.8 (GND), U1.9 (GND), U2.3 (GND), U2.8 (GND), U2.9 (GND), U3.3 (GND), U3.8 (GND), U3.9 (GND), U4.1 (IN-), U4.3 (OUT-)
unnamed: D1.2 (A), D2.2 (A), U4.4 (OUT+)
unnamed: J1.1, U1.7 (B01)
unnamed: J1.2, U1.6 (B02)
unnamed: J1.3, U1.5 (A02)
unnamed: J1.4, U1.4 (A01)
unnamed: J2.1, U2.7 (B01)
unnamed: J2.2, U2.6 (B02)
unnamed: J2.3, U2.5 (A02)
unnamed: J2.4, U2.4 (A01)
unnamed: J3.1, U3.7 (B01)
unnamed: J3.2, U3.6 (B02)
unnamed: J3.3, U3.5 (A02)
unnamed: J3.4, U3.4 (A01)

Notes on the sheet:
PWM pin is usually not used in this application and is always 1
Motor Driver 2
Power
Interfaces
Motor Driver 1
Motor Driver 3
Mechanical
Populate one of these diodes.
Micro Controller

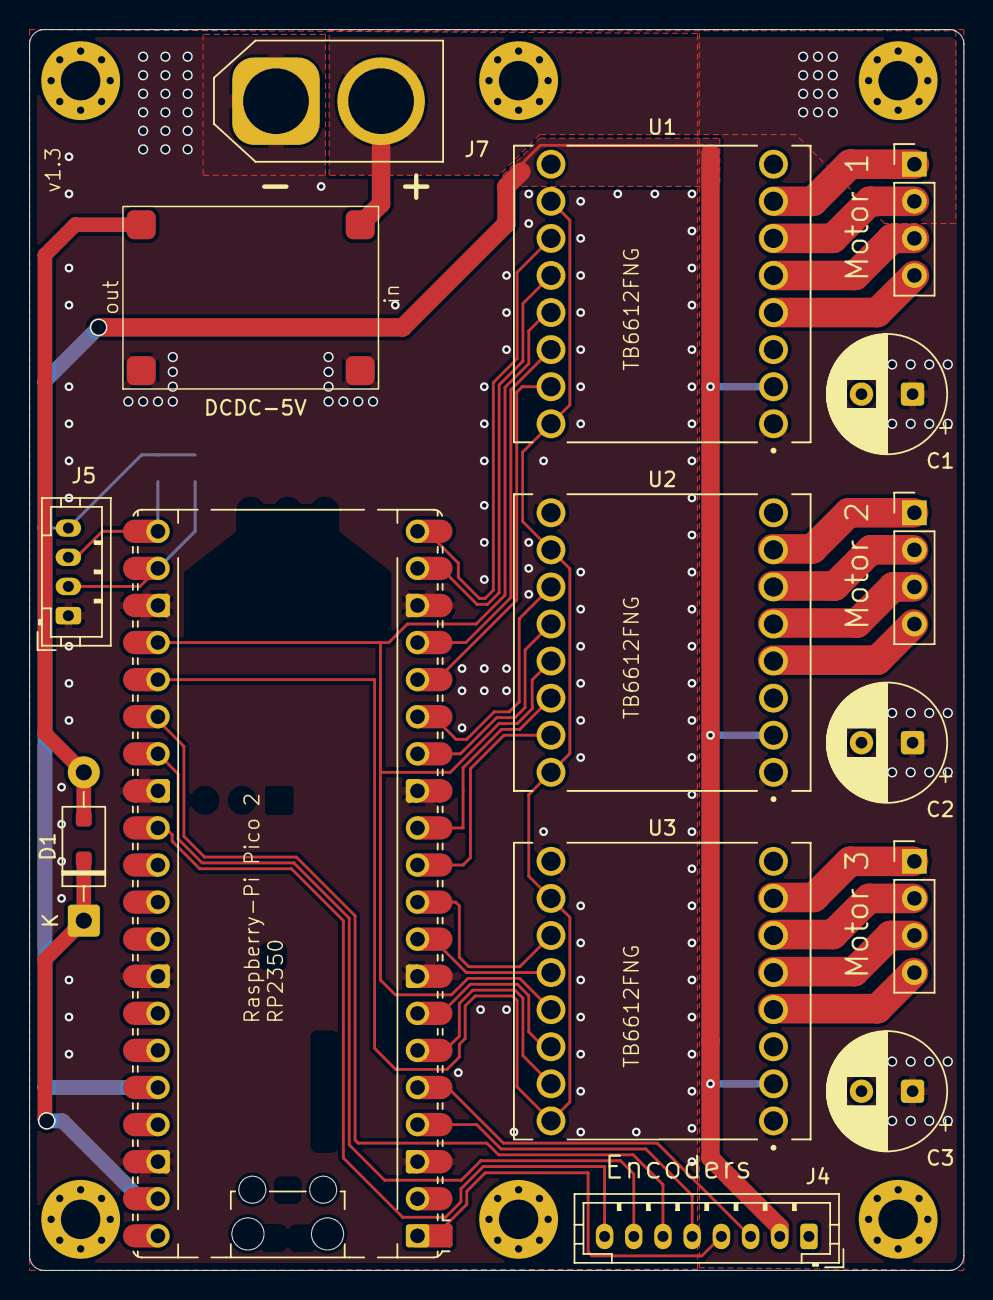
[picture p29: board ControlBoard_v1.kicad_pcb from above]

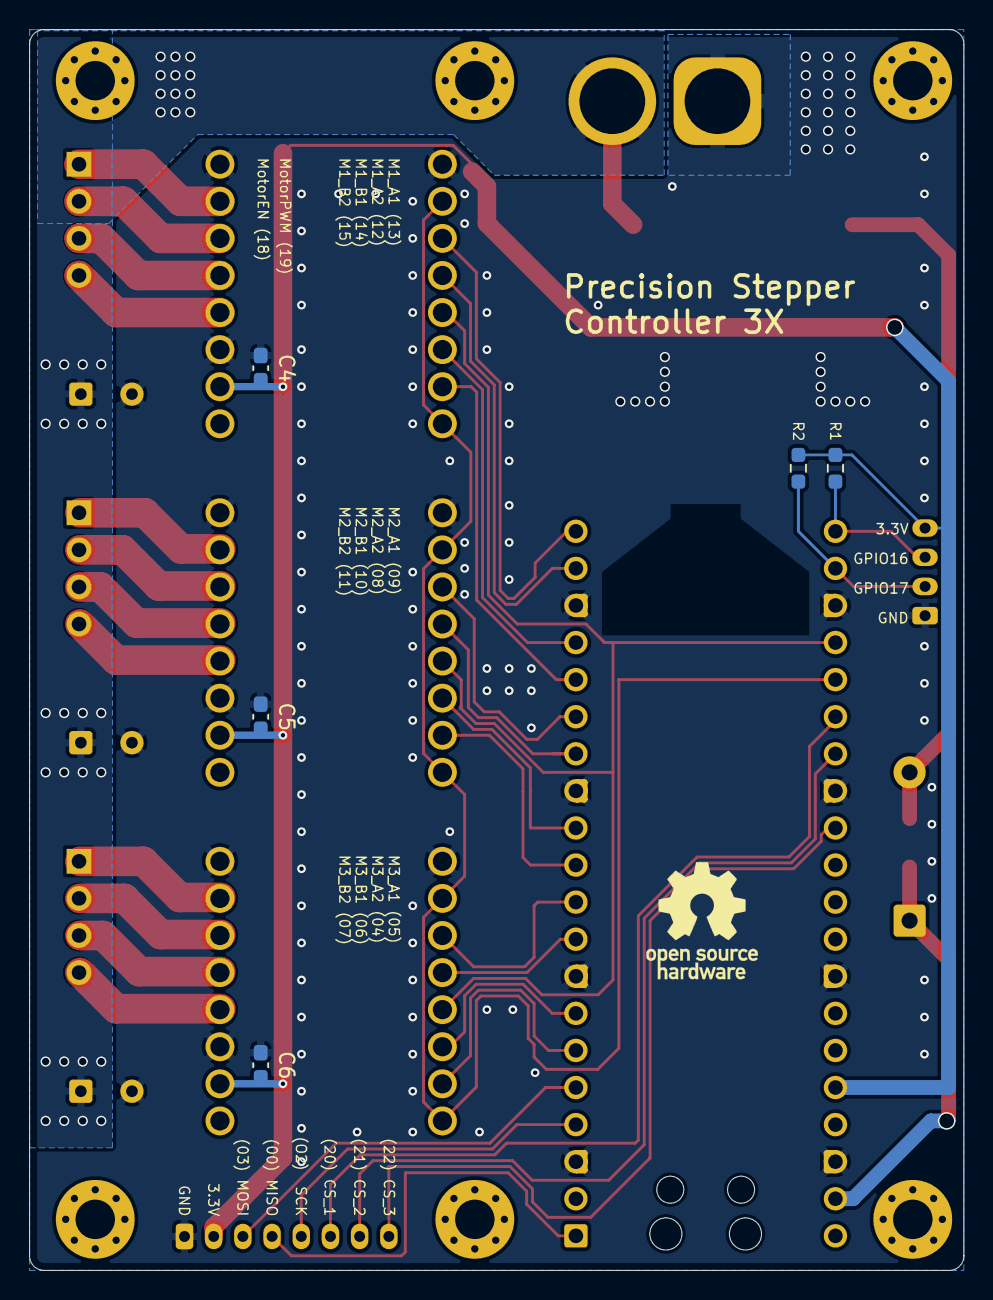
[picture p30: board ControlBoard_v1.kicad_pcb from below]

Board: 2 copper layers, 64.0 x 85.0 mm, 27 parts (6 on the bottom side), 39 nets.

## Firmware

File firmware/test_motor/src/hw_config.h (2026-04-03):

#pragma once
#include "utilities/math_constants.h"

//--- MOTORS ------------------------------------------------------------------

// motor pole pair count
//  * 100 for 0.9deg stepper motors
//  * 50  for 1.8deg stepper motors
constexpr float MOTOR1_POLE_PAIRS = 100;
constexpr float MOTOR2_POLE_PAIRS = 100;
constexpr float MOTOR3_POLE_PAIRS = 100;

//--- ENCODERS ----------------------------------------------------------------

// Conversion factor from encoder angle (one 2pi period every two magnets) to rotor angle.
// Used when the system can not rely on calibration data being present (e.g. during homing)
constexpr float ENCODER_MAGNET_PITCH = 3.0f;    // [mm]
constexpr float ENCODER_MAGNET_RADIUS = 30.0f;  // [mm]
constexpr float ENCODER_ANGLE_TO_ROTOR_ANGLE = (ENCODER_MAGNET_PITCH*2.0f) / 
                                               (ENCODER_MAGNET_RADIUS * Constants::TWO_PI_F);

//--- HOMING ------------------------------------------------------------------

constexpr float HOMING_VELOCITY   = 1.0f;        // rad per s
constexpr float HOMING_CURRENT    = 0.15f;       // range 0..1
constexpr float HOMING_FINISH_POS = 0.5f;        // in rad

//--- CALIBRATION -------------------------------------------------------------

// degrees from home position
constexpr float CALIBRATION_RANGE = 95; 

// velocity of the magnetic field during calibration (lower is more accurate)
constexpr float CALIBRATION_FIELD_VELOCITY = 40.0f; 

//--- PINS --------------------------------------------------------------------

// #define SINGLE_AXIS_BOARD
#ifndef SINGLE_AXIS_BOARD
  // Pins for 3Axis Board
  #define PIN_BUILTIN_LED 23
  #define PIN_USER_BUTTON 24

  #define PIN_M1_PWM_A_POS  13
  #define PIN_M1_PWM_A_NEG  12
  #define PIN_M1_PWM_B_POS  14
  #define PIN_M1_PWM_B_NEG  15

  #define PIN_M2_PWM_A_POS  9
  #define PIN_M2_PWM_A_NEG  8
  #define PIN_M2_PWM_B_POS  10
  #define PIN_M2_PWM_B_NEG  11

  #define PIN_M3_PWM_A_POS  5
  #define PIN_M3_PWM_A_NEG  4
  #define PIN_M3_PWM_B_POS  6
  #define PIN_M3_PWM_B_NEG  7


  #define PIN_MOTOR_EN      18
  #define PIN_MOTOR_PWMAB   19

  #define PIN_ENCODER1_CS 20
  #define PIN_ENCODER2_CS 21
  #define PIN_ENCODER3_CS 22
  #define PIN_ENCODER_SCK 2
  #define PIN_ENCODER_MISO 0
  #define PIN_ENCODER_MOSI 3

#else
  // Single Axis Board
  #define PIN_BUILTIN_LED 16
  #define PIN_USER_BUTTON 24

  #define PIN_M1_PWM_A_POS  13
  #define PIN_M1_PWM_A_NEG  12
  #define PIN_M1_PWM_B_POS  14
  #define PIN_M1_PWM_B_NEG  15

  #define PIN_M2_PWM_A_POS  9
  #define PIN_M2_PWM_A_NEG  8
  #define PIN_M2_PWM_B_POS  10
  #define PIN_M2_PWM_B_NEG  11

  #define PIN_M3_PWM_A_POS  5
  #define PIN_M3_PWM_A_NEG  4
  #define PIN_M3_PWM_B_POS  6
  #define PIN_M3_PWM_B_NEG  7


  #define PIN_MOTOR_EN      18
  #define PIN_MOTOR_PWMAB   19

  #define PIN_ENCODER1_CS 20
  #define PIN_ENCODER2_CS 21
  #define PIN_ENCODER3_CS 22
  #define PIN_ENCODER_SCK 2
  #define PIN_ENCODER_MISO 0
  #define PIN_ENCODER_MOSI 3
#endif

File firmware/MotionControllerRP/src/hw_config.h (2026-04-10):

#pragma once
#include "utilities/math_constants.h"

// #define DEMO_MODE

//--- MOTORS ------------------------------------------------------------------

// motor pole pair count
//  * 100 for 0.9deg stepper motors
//  * 50  for 1.8deg stepper motors
constexpr float MOTOR1_POLE_PAIRS = 50;
constexpr float MOTOR2_POLE_PAIRS = 50;
constexpr float MOTOR3_POLE_PAIRS = 50;

// max current factor in range [0..1]. Lower values reduce pwm resolution so a
// value above 0.4 is recommended.
constexpr float MOTOR_MAX_CURRENT_FACTOR = 0.6f;

//--- ENCODERS ----------------------------------------------------------------

// Conversion factor from encoder angle (one 2pi period every two magnets) to rotor angle.
// Used when the system can not rely on calibration data being present (e.g. during homing)
constexpr float ENCODER_MAGNET_PITCH = 3.0f;    // [mm]
constexpr float ENCODER_MAGNET_RADIUS = 30.0f;  // [mm]
constexpr float ENCODER_ANGLE_TO_ROTOR_ANGLE = (ENCODER_MAGNET_PITCH*2.0f) / 
                                               (ENCODER_MAGNET_RADIUS * Constants::TWO_PI_F);
											   
// enables error checking for encoders (slow) - useful for debugging
// Note: some chips seem to return always a crc of 0 producing massiv false errors       
constexpr bool ENABLE_ENCODER_CRC = false;

//--- HOMING ------------------------------------------------------------------

constexpr float HOMING_VELOCITY   = 1.0f;        // rad per s
constexpr float HOMING_CURRENT    = 0.5f;       // range 0..1
// NOT IMPLEMENTED YET: constexpr float HOMING_FINISH_POS = 0.5f;        // in rad
constexpr float HOMING_RETRACTION_FIELD_ANGLE = 8.0f;
constexpr float HOMING_RETRACTION_Z_FIELD_ANGLE = 2.0f;
constexpr float CALIBRATION_RETRACTION_FIELD_ANGLE = 0.25f;

//--- CALIBRATION -------------------------------------------------------------

// degrees from home position
constexpr float CALIBRATION_RANGE = 75; 

// velocity of the magnetic field during calibration (lower is more accurate)
constexpr float CALIBRATION_FIELD_VELOCITY = 20.0f; 

// size of the calibration lookup table
constexpr int ENCODER_LUT_SIZE = 256;

//--- CLOSED LOOP CONTROL -----------------------------------------------------

// position controller 
constexpr float POS_KP = 60.0f;
constexpr float POS_KI = 30000.0f;

// velocity controller
constexpr float VEL_LOWPASS_TC = 0.004f;
constexpr float VEL_KP = 0.2f;
constexpr float VEL_KI = 90.0f;

//--- KINEMATIC ---------------------------------------------------------------

// Kinematic Parameters are defined kinematic_modes/kinematic_model_delta3d.cpp

// NUM_JOINTS and NUM_TOOLS are defined in 'path_segment.h'. Note that changing
// the number of joints requires changing the kinematic model accordingly and
// also requires the initialization of the correct number of 'RobotJoint' objects
// in the Robtos init method.

//--- PERIPHERAL ------------------------------------------------------------------
#define PERIPHERAL_ENABLED true
#define PERIPHERAL_REQUIRED false
#define PERIPHERAL_I2C_ADDRESS 0x10
#define PERIPHERAL_I2C_INSTANCE i2c0
#define PERIPHERAL_I2C_SDA_PIN 16
#define PERIPHERAL_I2C_SCL_PIN 17
#define PERIPHERAL_I2C_CLOCK 30000

//--- PINS --------------------------------------------------------------------

#define JOINT_READY_OVERRIDE

// #define SINGLE_AXIS_BOARD
#ifndef SINGLE_AXIS_BOARD
  // Pins for 3Axis Board
  // #define PIN_BUILTIN_LED 23 // RP2040 pico clone
  // #define PIN_USER_BUTTON 24 // RP2040 pico clone
  #define PIN_BUILTIN_LED 25

  #define PIN_M1_PWM_A_POS  13
  #define PIN_M1_PWM_A_NEG  12
  #define PIN_M1_PWM_B_POS  14
  #define PIN_M1_PWM_B_NEG  15

  #define PIN_M2_PWM_A_POS  9
  #define PIN_M2_PWM_A_NEG  8
  #define PIN_M2_PWM_B_POS  10
  #define PIN_M2_PWM_B_NEG  11

  #define PIN_M3_PWM_A_POS  5
  #define PIN_M3_PWM_A_NEG  4
  #define PIN_M3_PWM_B_POS  6
  #define PIN_M3_PWM_B_NEG  7


  #define PIN_MOTOR_EN      18
  #define PIN_MOTOR_PWMAB   19

  #define PIN_ENCODER1_CS 20
  #define PIN_ENCODER2_CS 21
  #define PIN_ENCODER3_CS 22
  #define PIN_ENCODER_SCK 2
  #define PIN_ENCODER_MISO 0
  #define PIN_ENCODER_MOSI 3

  #define PIN_TOOL1 16
  #define PIN_TOOL2 17

#else
  // Single Axis Board
  #define PIN_BUILTIN_LED 16
  #define PIN_USER_BUTTON 24

  #define PIN_M1_PWM_A_POS  13
  #define PIN_M1_PWM_A_NEG  12
  #define PIN_M1_PWM_B_POS  14
  #define PIN_M1_PWM_B_NEG  15

  #define PIN_M2_PWM_A_POS  9
  #define PIN_M2_PWM_A_NEG  8
  #define PIN_M2_PWM_B_POS  10
  #define PIN_M2_PWM_B_NEG  11

  #define PIN_M3_PWM_A_POS  5
  #define PIN_M3_PWM_A_NEG  4
  #define PIN_M3_PWM_B_POS  6
  #define PIN_M3_PWM_B_NEG  7


  #define PIN_MOTOR_EN      18
  #define PIN_MOTOR_PWMAB   19

  #define PIN_ENCODER1_CS 20
  #define PIN_ENCODER2_CS 21
  #define PIN_ENCODER3_CS 22
  #define PIN_ENCODER_SCK 2
  #define PIN_ENCODER_MISO 0
  #define PIN_ENCODER_MOSI 3
#endif

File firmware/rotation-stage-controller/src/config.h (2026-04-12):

#if !defined(CONFIG_H)
#define CONFIG_H


// uncomment this to print debug messages through serial
#define DEBUG_PRINTS



/**
 * MT6835 Sensor
 */
#define SENSOR_MOSI PB5
#define SENSOR_MISO PB4
#define SENSOR_SCK PB3
#define SENSOR_SS PA15

#define MT6835_CPR 2097152



/**
 * PWM
 */

// The 72MHz clock cannot support 40kHz with 12-bit resolution, so the actual frequency will be lower
#define PWM_FREQ 40000
#define PWM_RES RESOLUTION_12B_COMPARE_FORMAT
#define PWM_MAX_VALUE 4096

#define MOT_A_POS PA_0
#define MOT_A_NEG PA_1
#define MOT_B_POS PA_2
#define MOT_B_NEG PA_3




/**
 * I2C
 */
#define I2C_SDA PB7
#define I2C_SCL PB6
#define I2C_SLAVE_ADDRESS 0x10


/**
 * Endstop & homing
 */
#define ROTATION_ENDSTOP PA12


/**
 * Heating
 */
#define TEMP_SENSOR_PIN PB0
#define HEATER_PIN PB1

/**
 * Control
 */

#define STEPPER_STEPS 50
#define LOOKUP_TABLE_SIZE (STEPPER_STEPS * 4 + 10) // 10 extra for safety margin



#define VAC_PWM_PIN  PB8          
#define VAC_PWM_FREQ 25000       
#define VAC_PWM_RES  RESOLUTION_12B_COMPARE_FORMAT
#define VAC_PWM_MAX  PWM_MAX_VALUE



#endif // CONFIG_H

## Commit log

2026-03-08 change to f103c8 board
2026-03-12 Update figures
    [output_1.csv]
2026-03-12 Current sorta working but not changes
    [output_0.csv, output_1.csv, output_2.csv]
2026-03-20 Updates and stuff for camera comparer
2026-03-30 Updates for script visualization
    [movement_tests.csv, movement_tests_short.csv]
2026-03-31 Update with better detection
    [movement_tests.csv, movement_tests_short.csv]
2026-04-01 Updates and stuff for feature identification
    [image_variation_results.csv, move_data.csv, movement_results.csv, progress.csv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]
2026-04-02 Update checks
    [image_variation_results.csv, variation_progress.csv]
2026-04-03 update temperature pid
2026-04-06 Cleanup code and stuff
    [data.csv, idx_to_coord.csv, image_variation_results.csv, movement_results.csv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]
2026-04-08 Continued improvements
    [output_1.csv, output_2.csv]
2026-04-21 add home and calibration debug command
